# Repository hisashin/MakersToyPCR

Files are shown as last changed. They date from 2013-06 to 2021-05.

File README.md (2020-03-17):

## [We're fighting with COVID-19 by upgrading NinjaPCR into affordable Real-Time PCR.](https://github.com/hisashin/NinjaPCR/wiki/NinjaPCR's-fight-with-COVID-19)

NinjaPCR is Opensource(GPLv3) DNA Amplifier,Thermocycler Implementation for [Polymerase Chain Reaction](http://en.wikipedia.org/wiki/Polymerase_chain_reaction) developed by [Shingo Hisakawa](https://www.facebook.com/hisakawa) and [Mariko Hisakawa](https://www.facebook.com/maripo).<br />

Check [support site](https://ninjapcr.tori.st) for more infomations including how to [make](https://ninjapcr.tori.st/maker/) it. BOM is [here](https://docs.google.com/spreadsheets/d/1QYWESJrQ2N63OPvq1pnQvB-iVQkymN-hYeTYLx7xuOw/edit?usp=sharing).

(https://ninjapcr.tori.st)

Forked from [OpenPCR](https://github.com/jperfetto/OpenPCR).

Major changes from OpenPCR:<br />
01. Smaller and [easier to build](https://ninjapcr.tori.st/assy/index.html)<br />
02. Change platform from Adobe AIR to WiFi. Almost all PC and smartphones are supported<br />
03. LCD removed. Everything on Browser<br />
04. Keep precision from low to high temperature<br />
05. Auto update for new features (ex. IFTTT support scheduled)<br />
06. It's still [on sale](https://shop.tori.st) (OpenPCR is [discontinued](https://www.chaibio.com/openpcr))

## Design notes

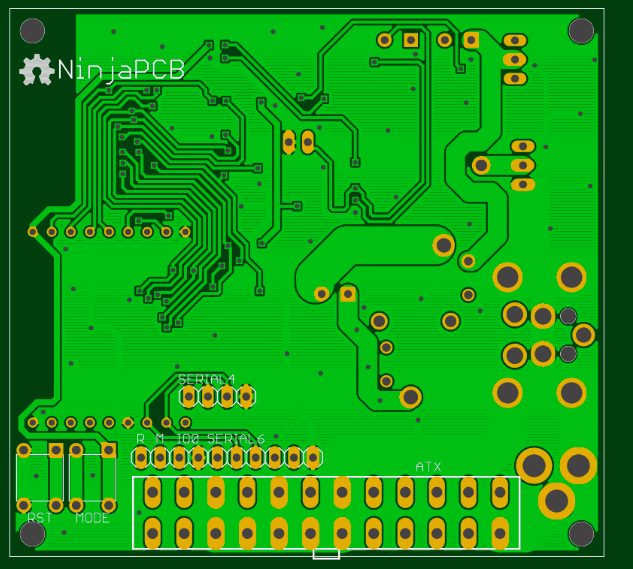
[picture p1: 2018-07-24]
eagle/NinjaPCB_ver2.2-bottom.png

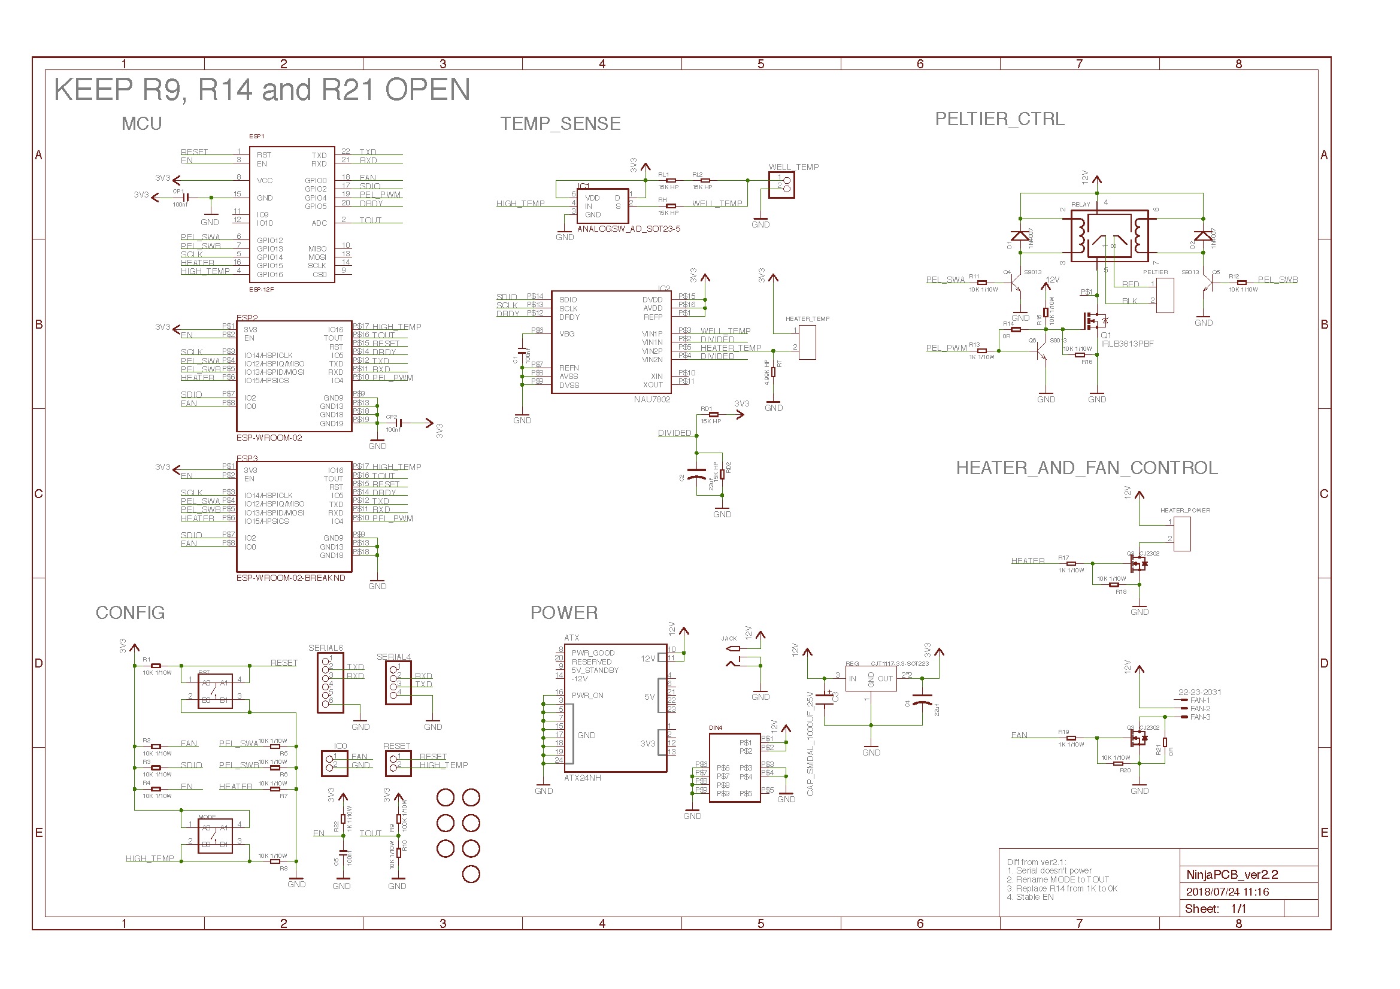
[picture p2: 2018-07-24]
eagle/NinjaPCB_ver2.2-sch.jpeg

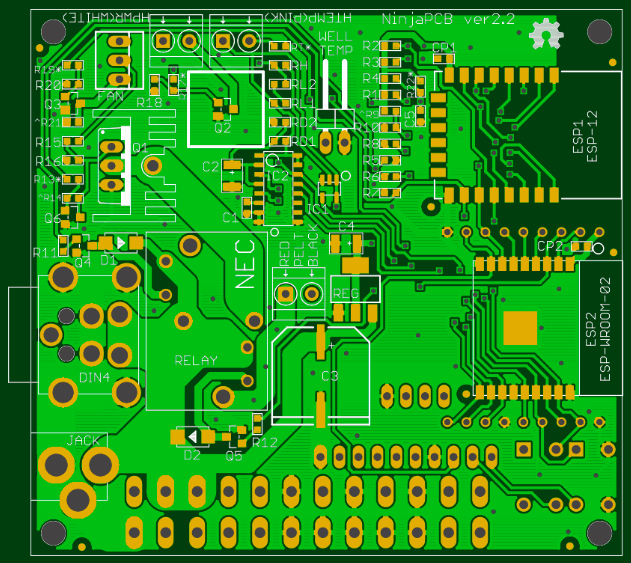
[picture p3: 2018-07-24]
eagle/NinjaPCB_ver2.2-top.png

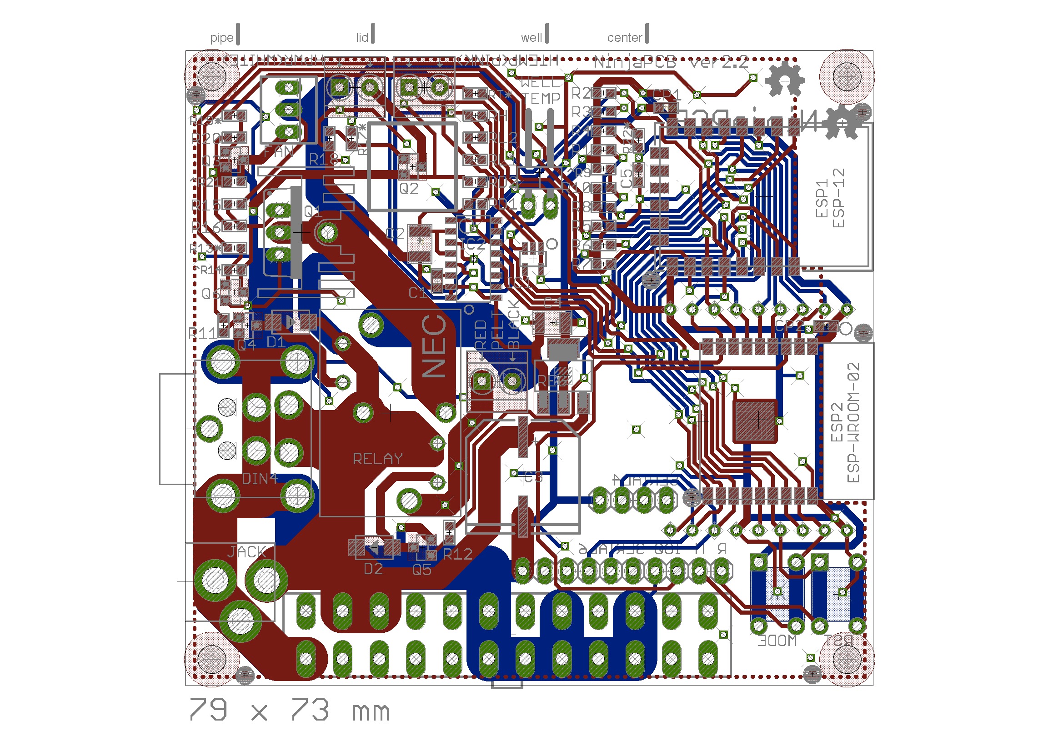
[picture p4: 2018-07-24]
eagle/NinjaPCB_ver2.2-brd.jpeg

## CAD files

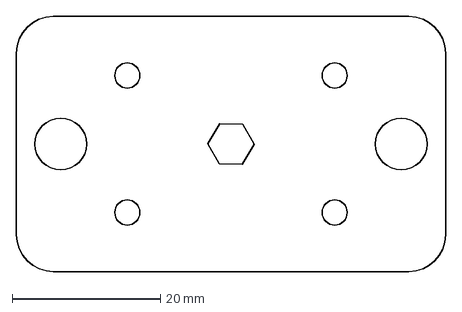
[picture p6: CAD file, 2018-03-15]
cad/2d/2x2-MooMoo/w4001_heater-lift.dxf
58.0 x 34.5 mm

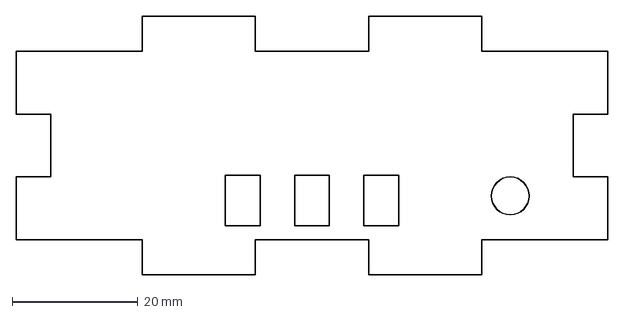
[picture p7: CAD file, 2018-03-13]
cad/2d/4x4-NinNin/w1003_cover-back.dxf
94.0 x 41.0 mm

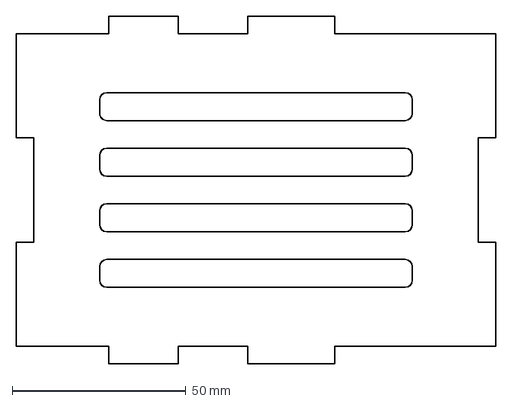
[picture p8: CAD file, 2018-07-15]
cad/2d/dxf-t5.0mm/LGA115x-kit/w2004.dxf
138.1 x 100.0 mm

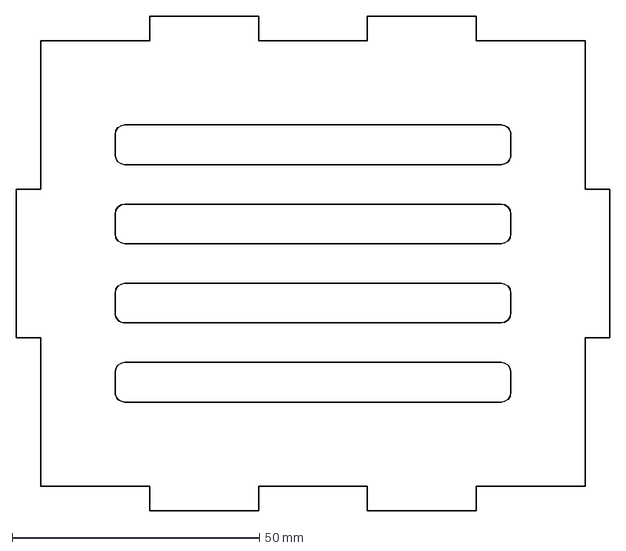
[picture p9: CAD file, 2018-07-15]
cad/2d/dxf-t5.0mm/w2005.dxf
120.0 x 100.0 mm

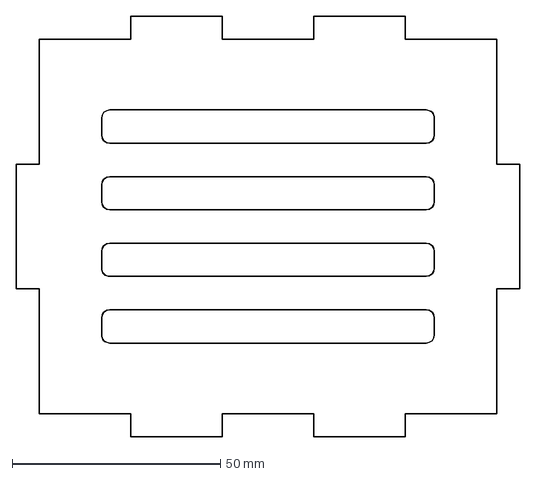
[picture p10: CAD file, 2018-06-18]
cad/2d/dxf-t5.5mm/LGA115x-kit/w2005.dxf
121.0 x 101.0 mm

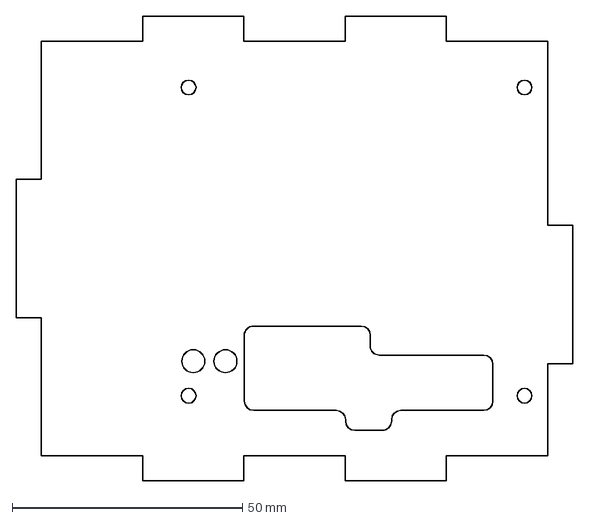
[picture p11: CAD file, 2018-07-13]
cad/2d/dxf-t5.5mm/LGA115x-maker/w2003-maker.dxf
121.0 x 101.0 mm

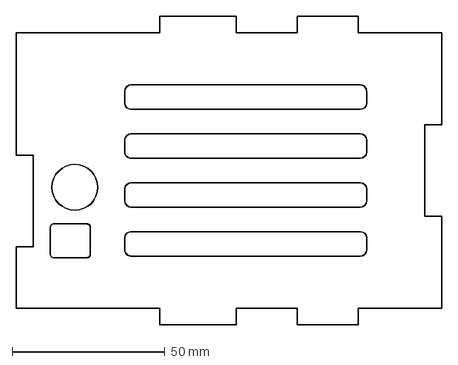
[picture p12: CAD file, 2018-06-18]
cad/2d/dxf-t5.5mm/LGA775-kit/w2006.dxf
139.1 x 101.0 mm

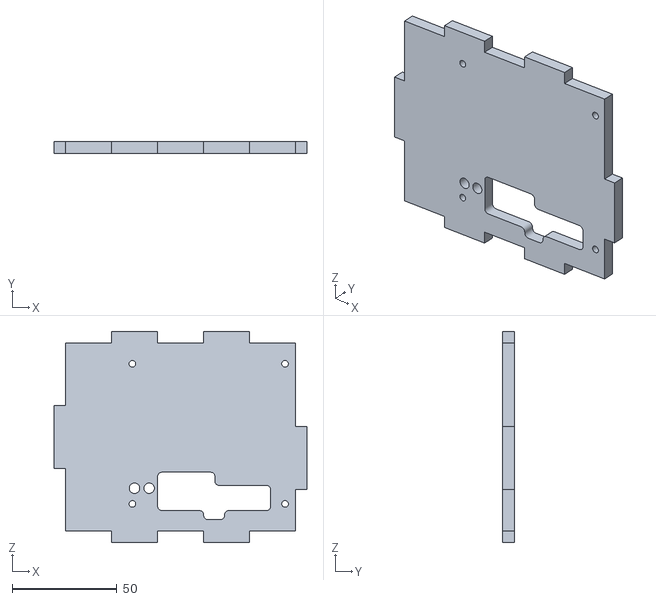
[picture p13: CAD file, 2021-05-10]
cad/3d/w2003a_body-front-ver2.1-maker.stl
121.0 x 5.50 x 101.0

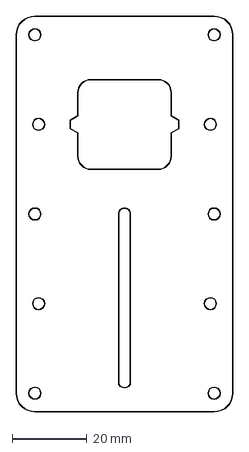
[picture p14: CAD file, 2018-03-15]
cad/2d/2x2-MooMoo/w4002-body-top.dxf
58.0 x 106.0 mm

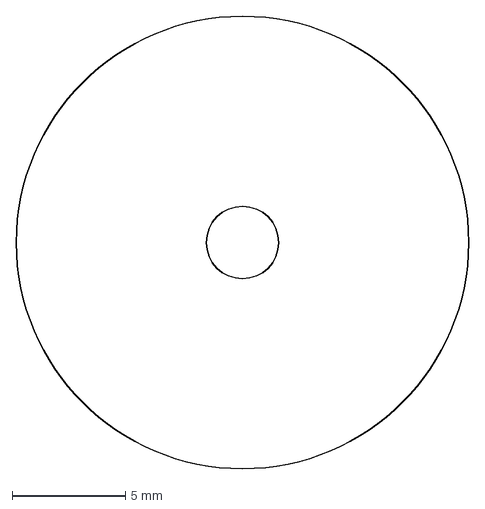
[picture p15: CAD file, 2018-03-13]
cad/2d/4x4-NinNin/w3003_latch-base.dxf
20.0 x 20.0 mm

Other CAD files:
cad/2d/2x2-MooMoo/w4004-heatsink-hold.dxf
cad/2d/4x4-NinNin/w1005_cover-sides.dxf
cad/2d/4x4-NinNin/w2001_heatsink-hang.dxf
cad/2d/4x4-NinNin/w2002_body-top.dxf
cad/2d/4x4-NinNin/w2004_body-left.dxf
cad/2d/4x4-NinNin/w2006_body-front.dxf
cad/2d/4x4-NinNin/w2008_body-hinges.dxf
cad/2d/dxf-t5.0mm/LGA115x-kit/w1001.dxf
cad/2d/dxf-t5.0mm/LGA115x-kit/w1002.dxf
cad/2d/dxf-t5.0mm/LGA115x-kit/w1003-kit.dxf
cad/2d/dxf-t5.0mm/LGA115x-kit/w1004-kit.dxf
cad/2d/dxf-t5.0mm/LGA115x-kit/w1005x2.dxf
cad/2d/dxf-t5.0mm/LGA115x-kit/w1006.dxf
cad/2d/dxf-t5.0mm/LGA115x-kit/w2001-LGA115x.dxf
cad/2d/dxf-t5.0mm/LGA115x-kit/w2002-LGA115x-kit.dxf
cad/2d/dxf-t5.0mm/LGA115x-kit/w2003-kit.dxf
cad/2d/dxf-t5.0mm/LGA115x-kit/w2003.dxf
cad/2d/dxf-t5.0mm/LGA115x-kit/w2006.dxf
cad/2d/dxf-t5.0mm/LGA115x-kit/w2007.dxf
cad/2d/dxf-t5.0mm/LGA115x-maker/w1001.dxf
cad/2d/dxf-t5.0mm/LGA115x-maker/w1002.dxf
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

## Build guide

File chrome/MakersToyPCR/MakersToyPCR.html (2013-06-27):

Makers Toy PCR

 Add a new experiment

 Re-run an experiment

Searching for a device...

Open Download Page



 Initial Step

 Final Step

Name your experiment

Experiment saved!

Delete Experiment?

Deleted!

Time remaining:

Status | Current Temperature
Cycle - / - | Lid: | °C
| Block: | °C
| Lid: Peltier:

Your Makers Toy PCR is unplugged from the computer.
Plug in your Makers Toy PCR to get updated information on your run.

Stop PCR?

Version
Makers Toy PCR App
http://www.tori.st
Email us: all@tori.st

Drag the slider to adjust the screen's contrast.

Ready. Steady. Go!

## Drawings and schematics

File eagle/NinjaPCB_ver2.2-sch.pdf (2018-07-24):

# TEMP_SENSE

MCU | PELTIER_CTRL

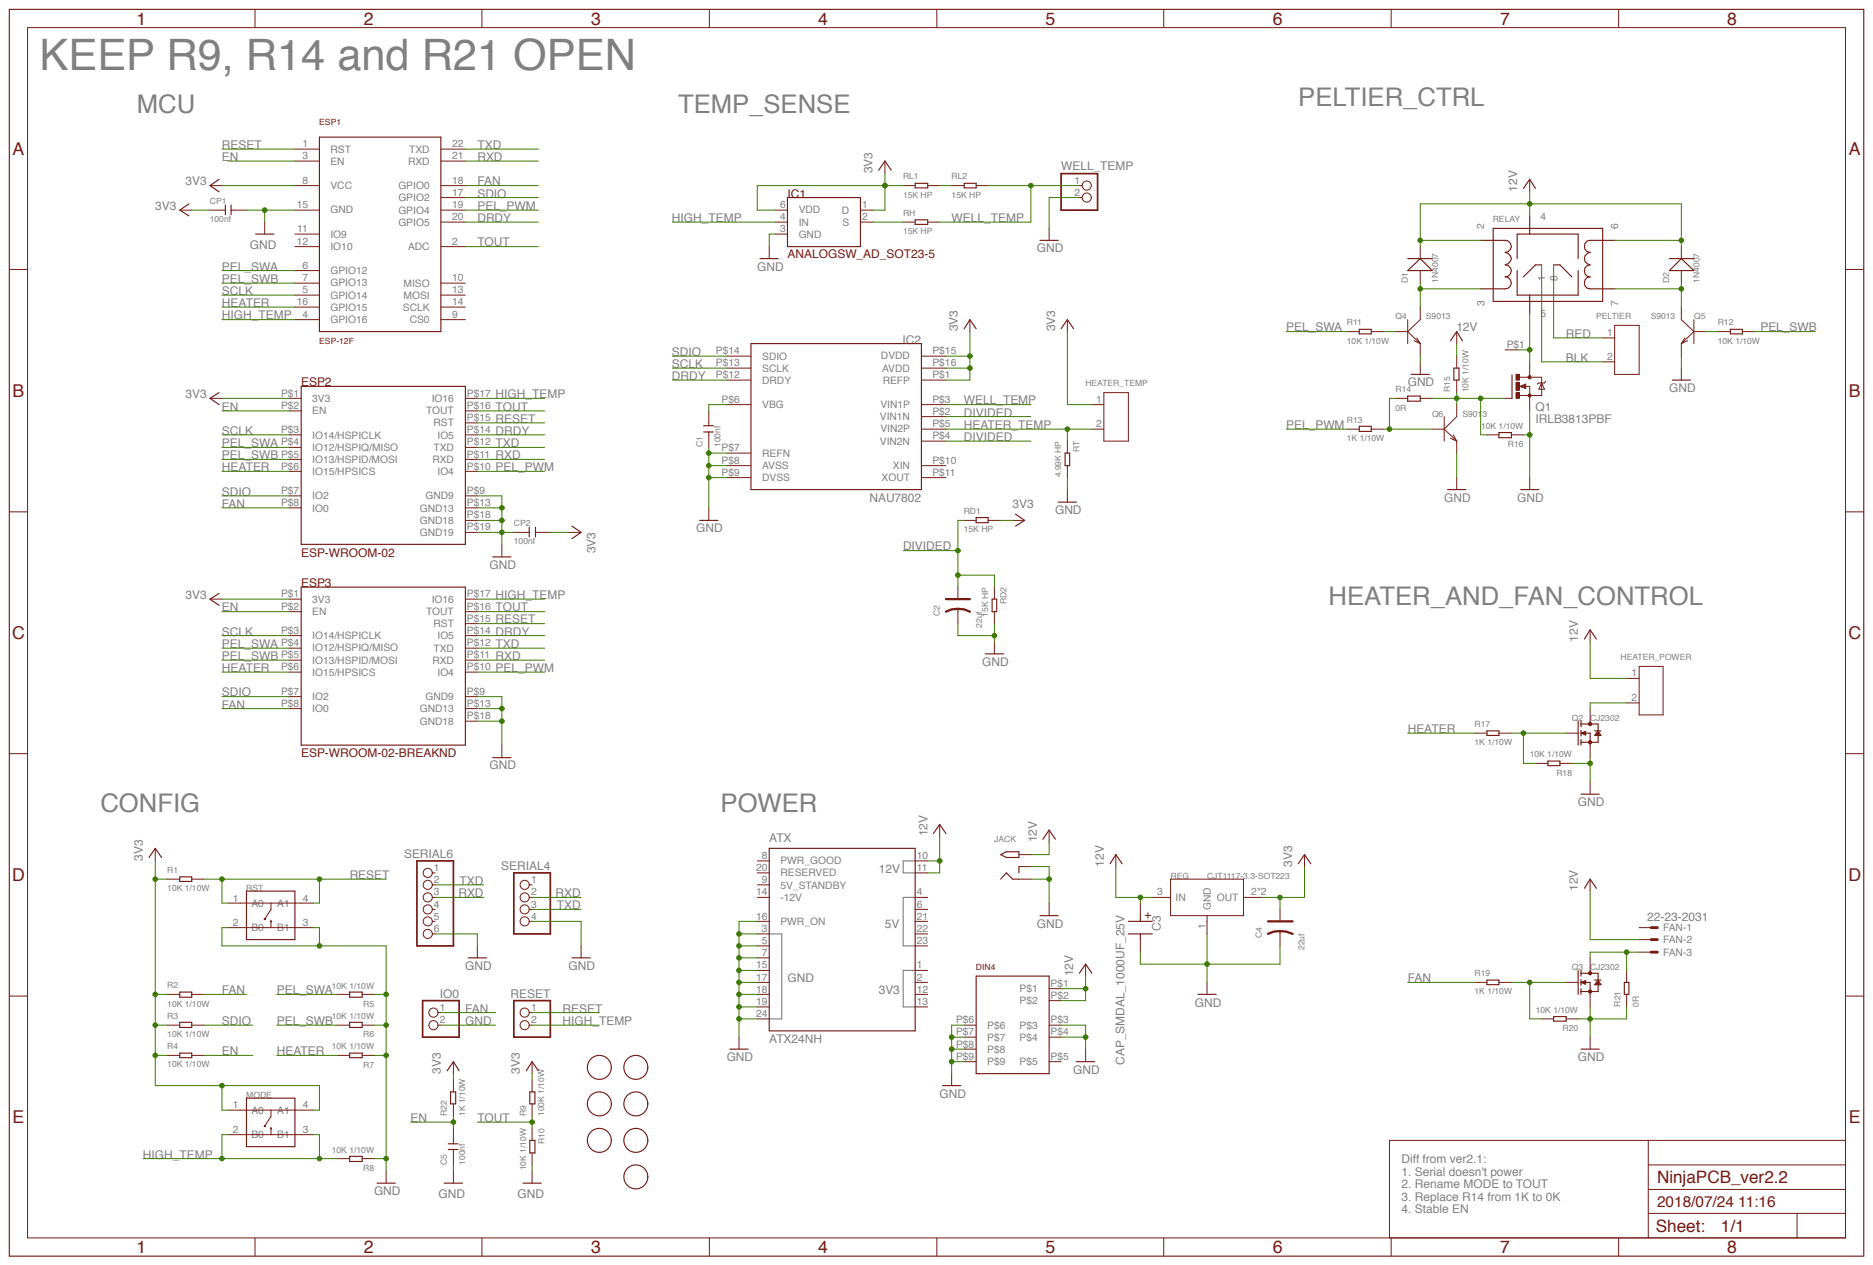
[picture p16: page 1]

Diff from ver2.1: 1. Serial doesn't power 2. Rename MODE to TOUT 3. Replace R14 from 1K to 0K 4. Stable EN

Sheet: 1/1

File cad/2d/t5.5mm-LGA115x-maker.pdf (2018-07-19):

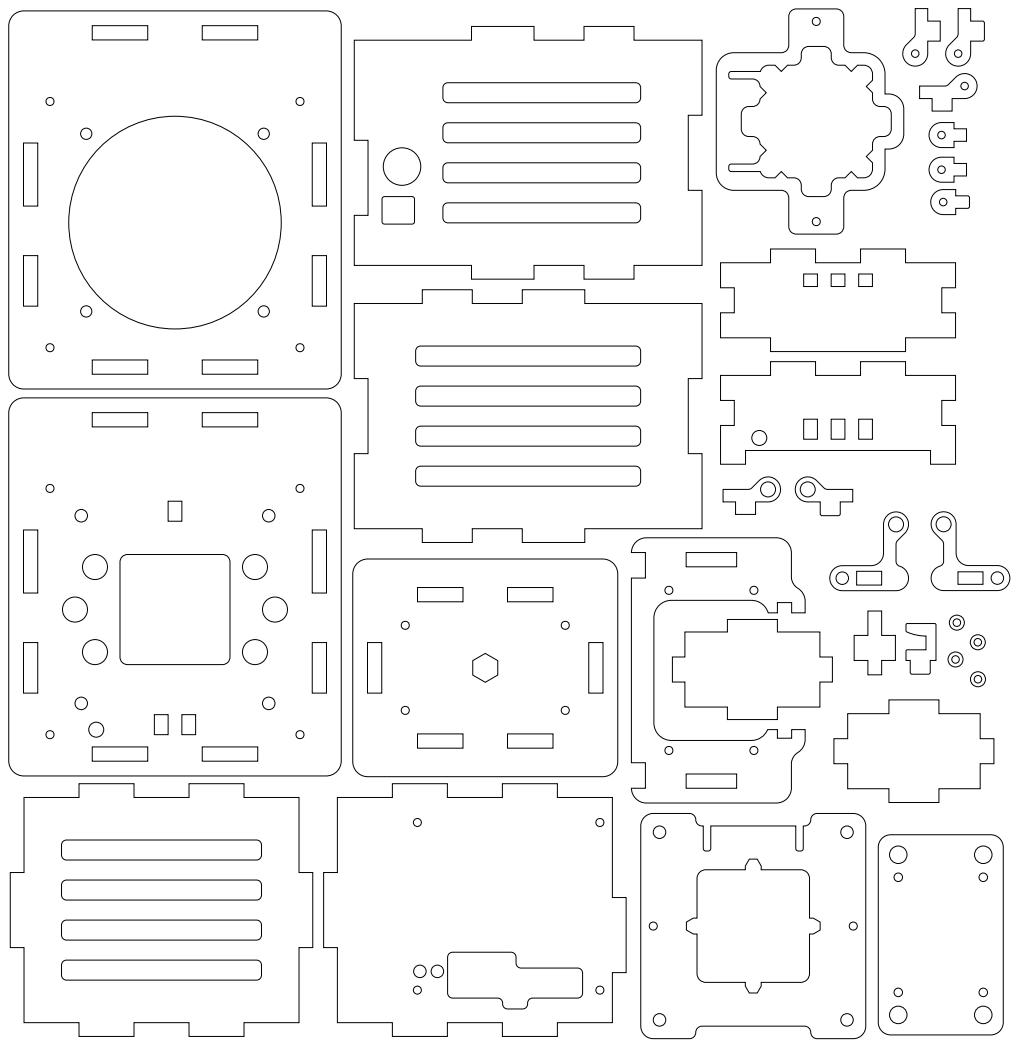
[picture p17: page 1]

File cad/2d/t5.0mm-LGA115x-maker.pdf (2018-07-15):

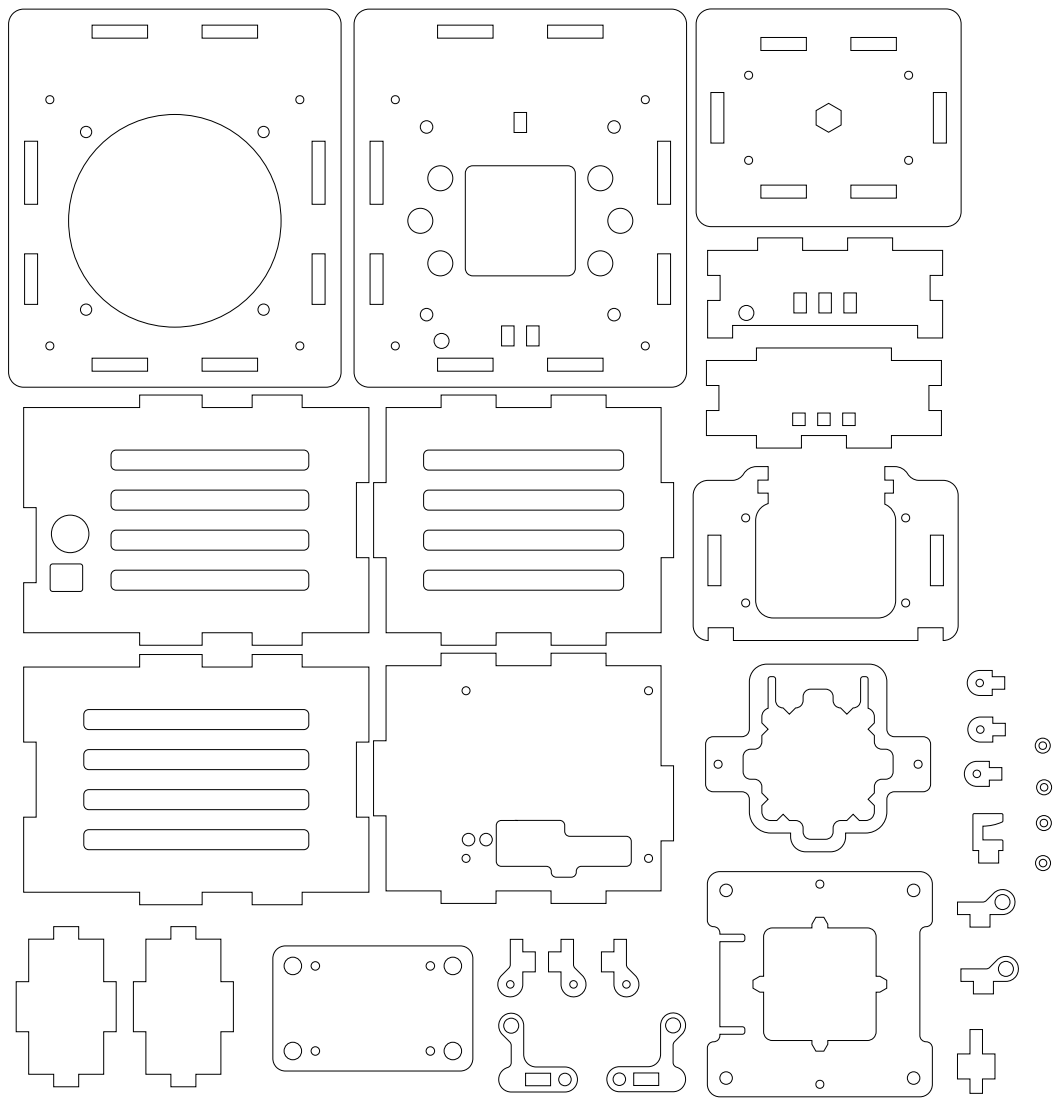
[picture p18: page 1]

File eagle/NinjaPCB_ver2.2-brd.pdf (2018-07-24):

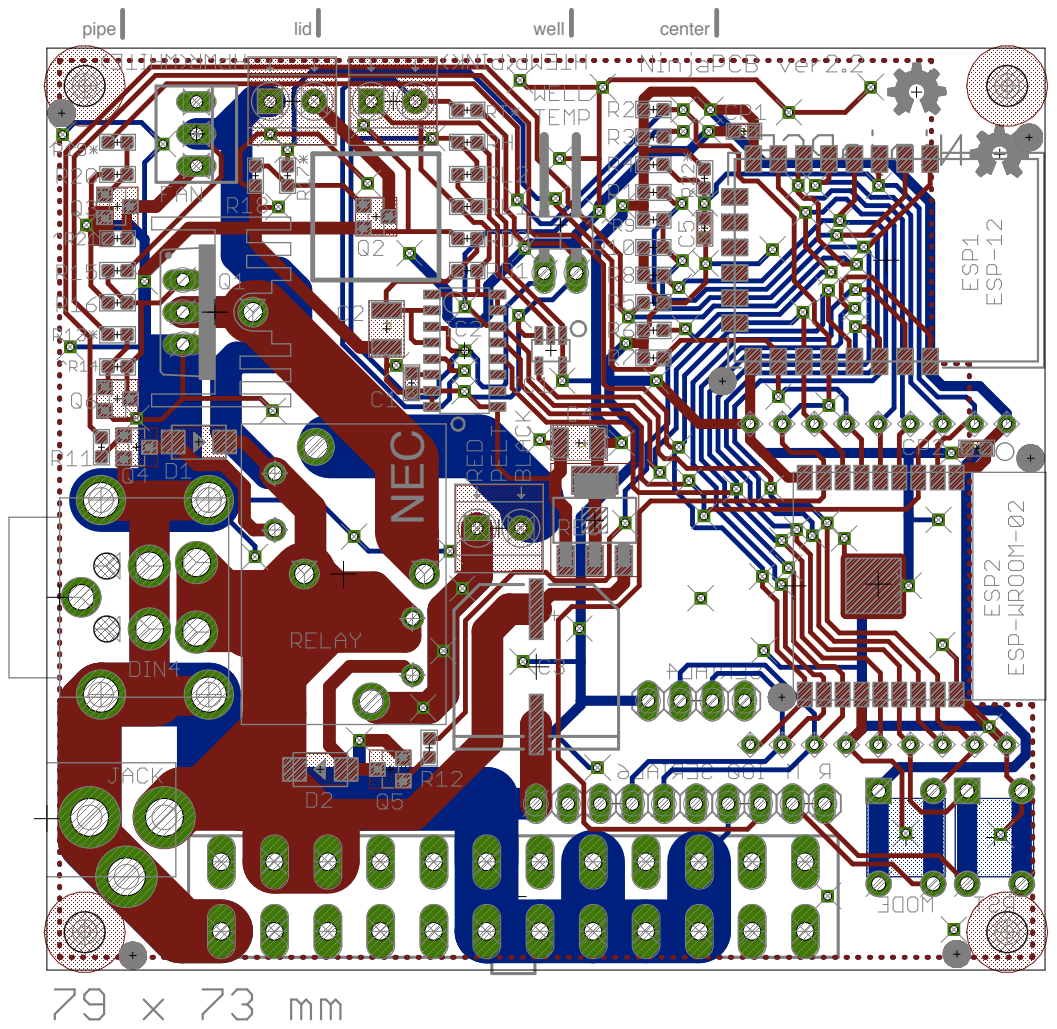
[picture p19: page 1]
NEC; pipe; lid; well; center

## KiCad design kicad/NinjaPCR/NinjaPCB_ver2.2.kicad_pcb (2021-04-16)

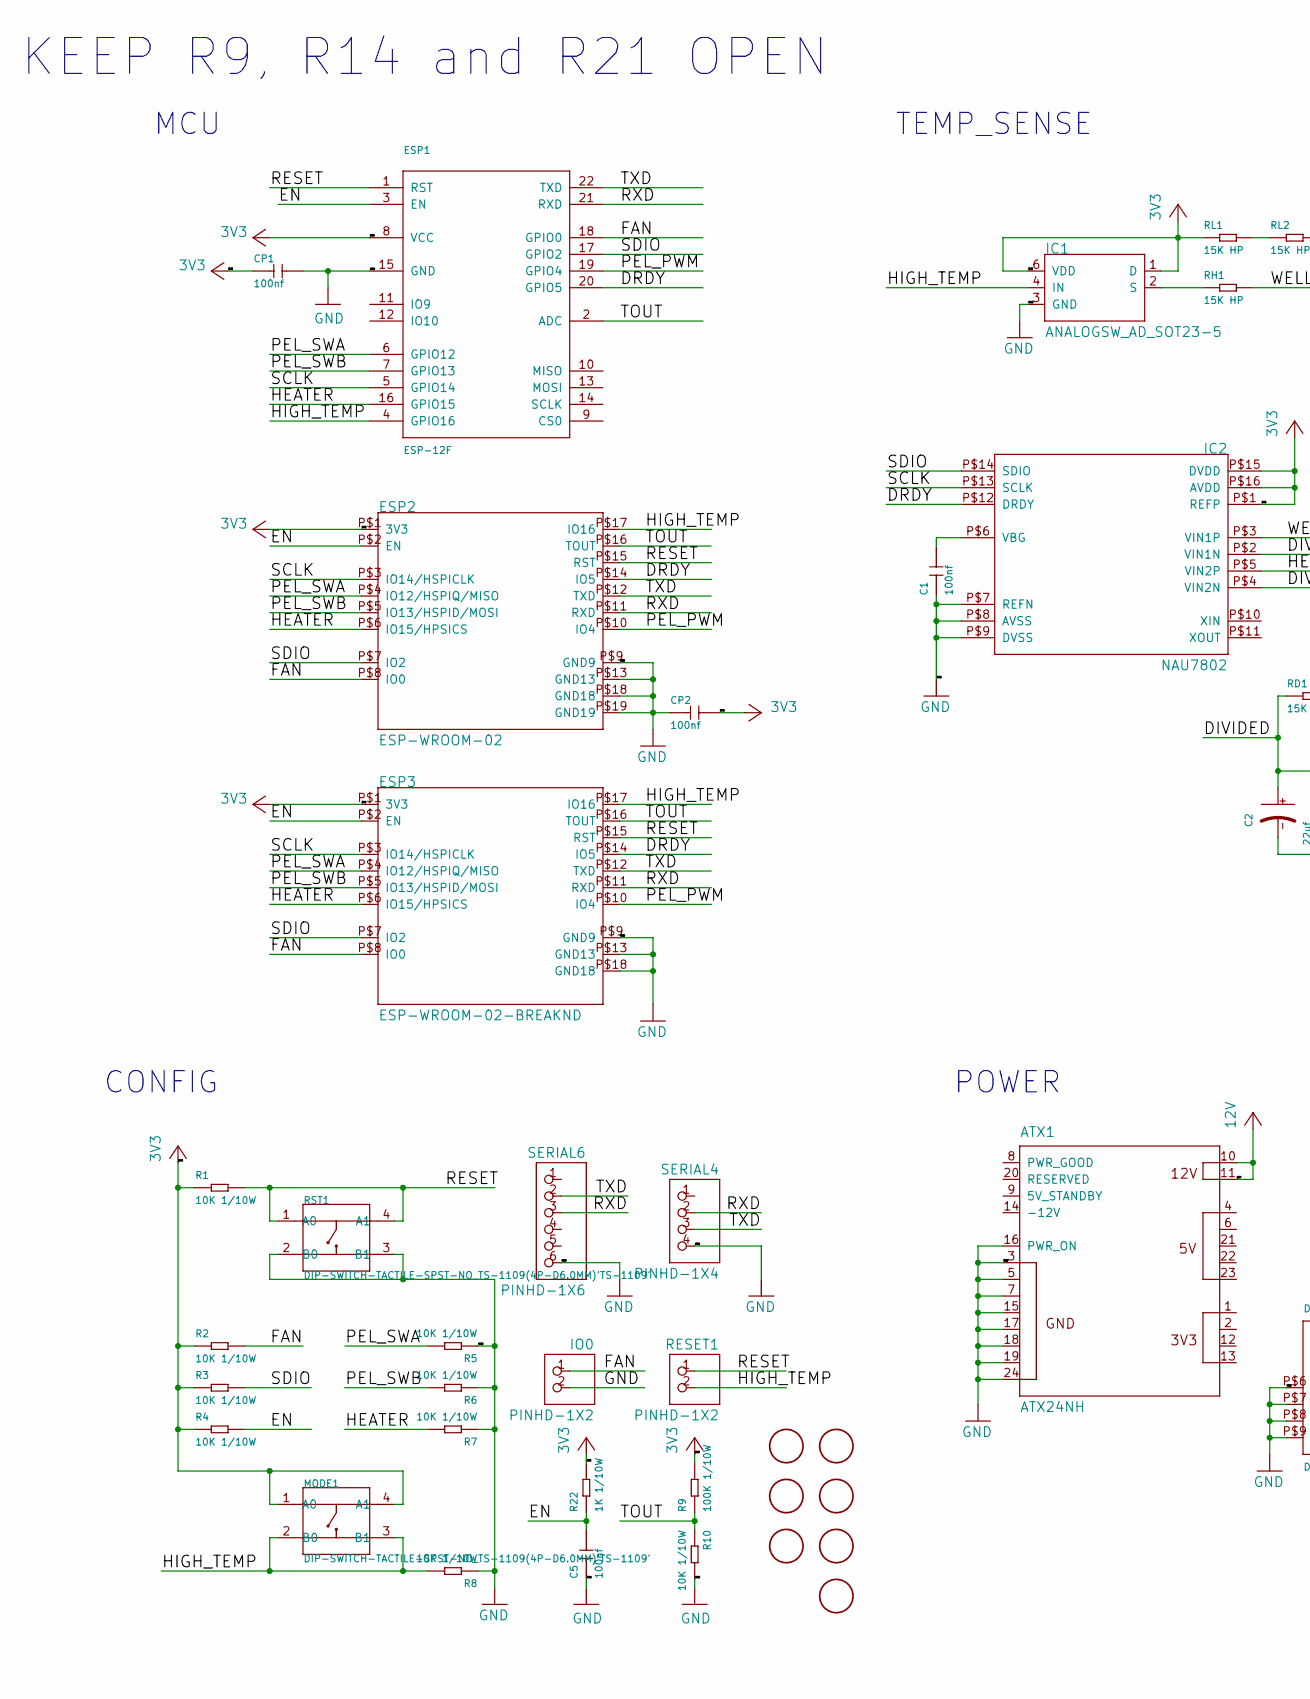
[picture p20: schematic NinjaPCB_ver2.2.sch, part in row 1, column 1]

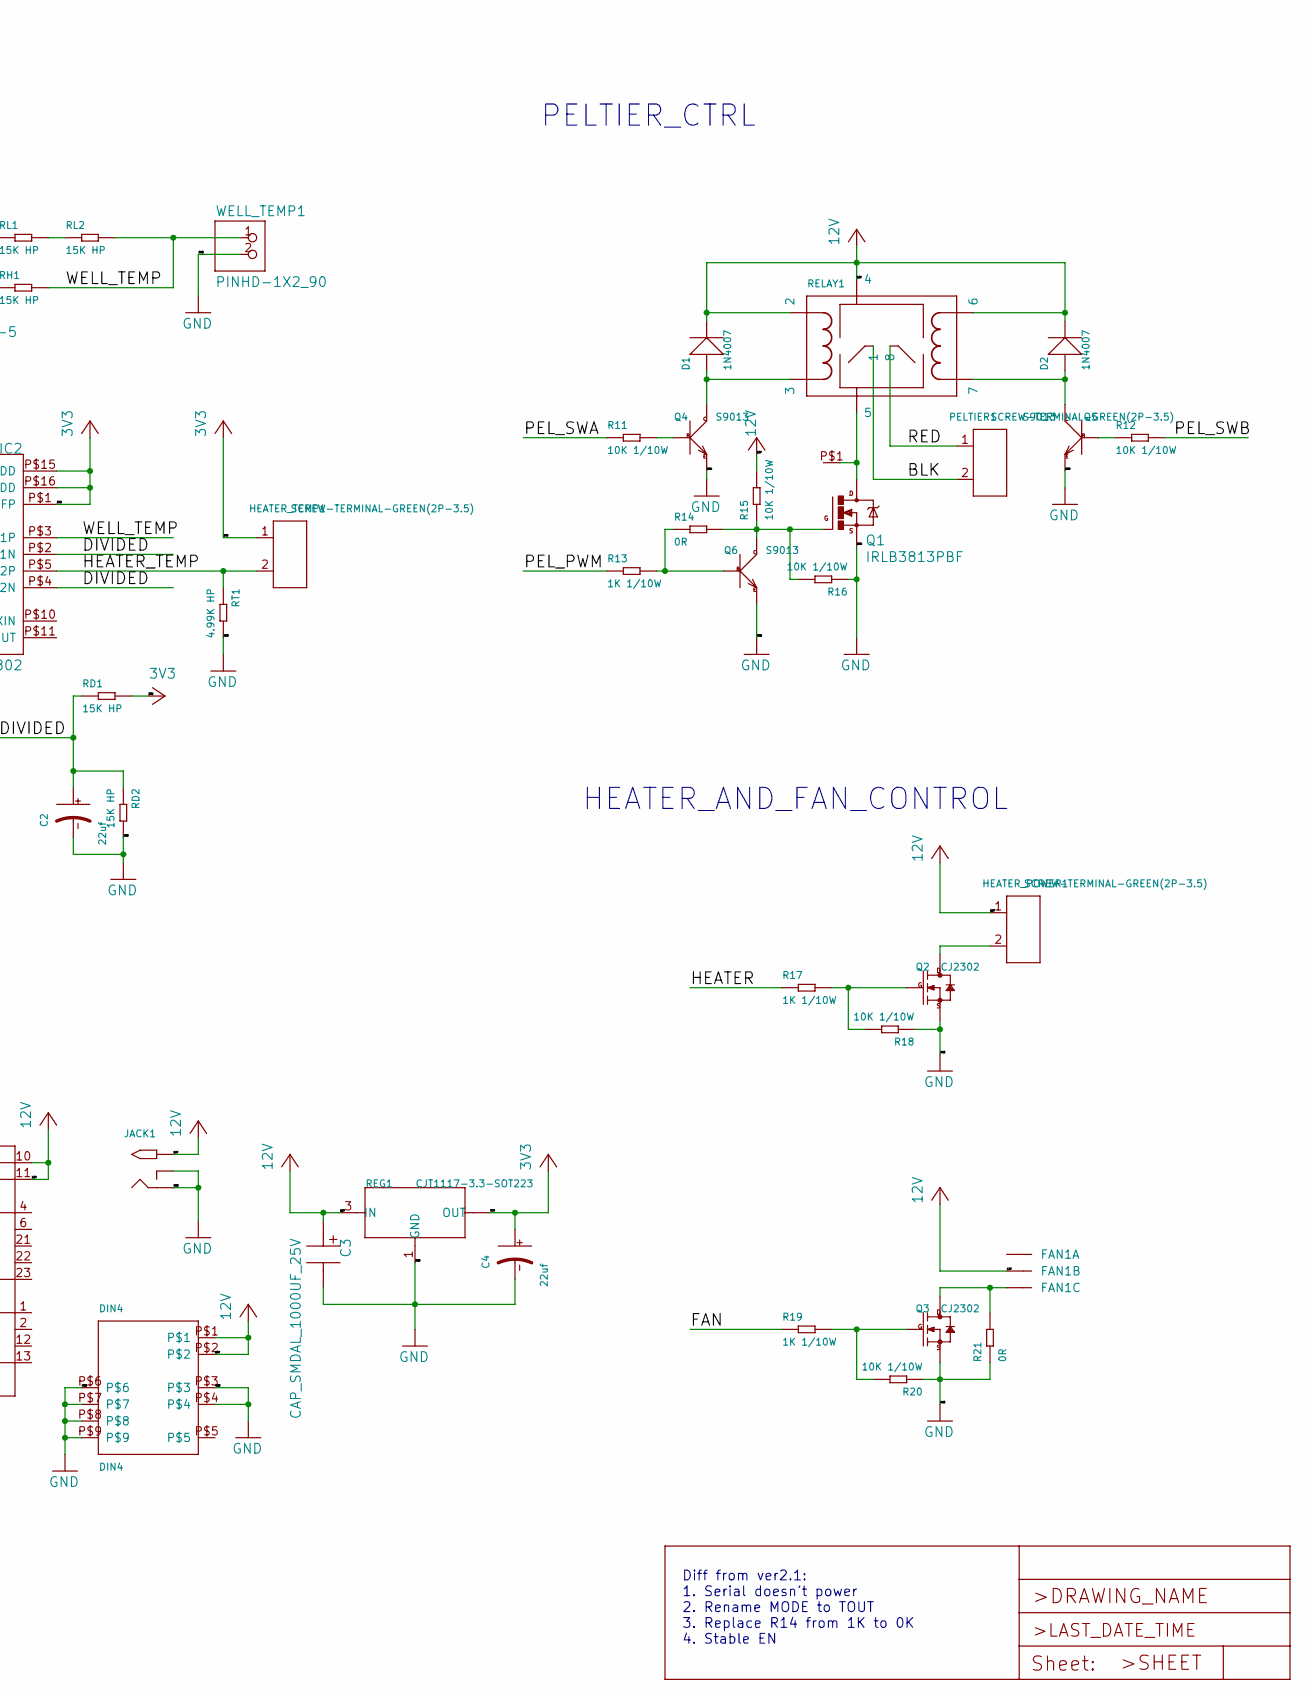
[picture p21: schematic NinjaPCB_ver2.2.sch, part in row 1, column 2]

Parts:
ATX1: ATX24NH; ATX24
C1, C5: 100nf; C0603
C2, C4: 22uf; AVX-B
C3: CAP_SMDAL_1000UF_25V; CAP_SMD_AL_D125
CP1, CP2: 100nf; C0603
D1, D2: 1N4007; DO-214AC
DIN4: DIN4
ESP1: ESP-12F
ESP2: ESP-WROOM-02
ESP3: ESP-WROOM-02-BREAKND; ESP-WROOM-02-BREAK-NODETAIL
FAN1: 22-23-2031
HEATER_POWER1: SCREW-TERMINAL-GREEN(2P-3.5); H2-3.5-7.0X7.0MM
HEATER_TEMP1: SCREW-TERMINAL-GREEN(2P-3.5); H2-3.5-7.0X7.0MM
HEATSINK1: HEAT111PB015; HEAT11PB015
IC1: ANALOGSW_AD_SOT23-5; SOT23-5
IC2: NAU7802; SOP-16
IO0: PINHD-1X2; 1X02
JACK1: 2.1MMJACKTHM-NOOUT; PJ-102A-NOOUT
MODE1: DIP-SWITCH-TACTILE-SPST-NO_TS-1109(4P-D6.0MM)'TS-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; SW4-6.0X6.0X5.0MM
PELTIER1: SCREW-TERMINAL-GREEN(2P-3.5); H2-3.5-7.0X7.0MM
Q1: IRLB3813PBF; TO220BV
Q2, Q3: CJ2302; SOT-23
Q4, Q5, Q6: S9013; SOT-23
R1, R2, R3, R4, R5, R6, R7, R8, R10, R11, R12, R15, R16, R18, R20: 10K 1/10W; R0603
R9: 100K 1/10W; R0603
R13, R17, R19, R22: 1K 1/10W; R0603
R14, R21: 0R; R0603
RD1, RD2: 15K HP; R0603
REG1: CJT1117-3.3-SOT223; SOT-223
RELAY1: NEC-RELAY2EP2; NEC-EP2
RESET1: PINHD-1X2; 1X02
RH1: 15K HP; R0603
RL1, RL2: 15K HP; R0603
RST1: DIP-SWITCH-TACTILE-SPST-NO_TS-1109(4P-D6.0MM)'TS-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; SW4-6.0X6.0X5.0MM
RT1: 4.99K HP; R0603
SERIAL4: PINHD-1X4; 1X04
SERIAL6: PINHD-1X6; 1X06
U$3, U$4, U$5, U$7, U$8, U$9, U$10: FIDUCIAL; FIDUCIAL_1MM
WELL_TEMP1: PINHD-1X2_90; 1X02_90

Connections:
/BLK: PELTIER1.2, RELAY1.P$1 (1)
/DIVIDED: C2.+, IC2.P$2 (VIN1N), IC2.P$4 (VIN2N), RD1.1, RD2.1
/DRDY: ESP1.20 (GPIO5), ESP2.P$14 (IO5), ESP3.P$14 (IO5), IC2.P$12 (DRDY)
/EN: C5.2, ESP1.3 (EN), ESP2.P$2 (EN), ESP3.P$2 (EN), R4.2, R22.1
/FAN: ESP1.18 (GPIO0), ESP2.P$8 (IO0), ESP3.P$8 (IO0), IO0.1, R2.2, R19.1
/HEATER: ESP1.16 (GPIO15), ESP2.P$6 (IO15/HPSICS), ESP3.P$6 (IO15/HPSICS), R7.2, R17.1
/HEATER_TEMP: HEATER_TEMP1.2, IC2.P$5 (VIN2P), RT1.1
/HIGH_TEMP: ESP1.4 (GPIO16), ESP2.P$17 (IO16), ESP3.P$17 (IO16), IC1.4 (IN), MODE1.2 (B0), MODE1.3 (B1), R8.2, RESET1.2
/PEL_PWM: ESP1.19 (GPIO4), ESP2.P$10 (IO4), ESP3.P$10 (IO4), R13.1
/PEL_SWA: ESP1.6 (GPIO12), ESP2.P$4 (IO12/HSPIQ/MISO), ESP3.P$4 (IO12/HSPIQ/MISO), R5.2, R11.1
/PEL_SWB: ESP1.7 (GPIO13), ESP2.P$5 (IO13/HSPID/MOSI), ESP3.P$5 (IO13/HSPID/MOSI), R6.2, R12.2
/RED: PELTIER1.1, RELAY1.P$8 (8)
/RESET: ESP1.1 (RST), ESP2.P$15 (RST), ESP3.P$15 (RST), R1.2, RESET1.1, RST1.1 (A0), RST1.4 (A1)
/RXD: ESP1.21 (RXD), ESP2.P$11 (RXD), ESP3.P$11 (RXD), SERIAL4.2, SERIAL6.3
/SCLK: ESP1.5 (GPIO14), ESP2.P$3 (IO14/HSPICLK), ESP3.P$3 (IO14/HSPICLK), IC2.P$13 (SCLK)
/SDIO: ESP1.17 (GPIO2), ESP2.P$7 (IO2), ESP3.P$7 (IO2), IC2.P$14 (SDIO), R3.2
/TOUT: ESP1.2 (ADC), ESP2.P$16 (TOUT), ESP3.P$16 (TOUT), R9.1, R10.1
/TXD: ESP1.22 (TXD), ESP2.P$12 (TXD), ESP3.P$12 (TXD), SERIAL4.3, SERIAL6.2
/WELL_TEMP: IC2.P$3 (VIN1P), RH1.2, RL2.2, WELL_TEMP1.1
GND: ATX1.3 (GND3), ATX1.5 (GND5), ATX1.7 (GND7), ATX1.15 (GND15), ATX1.16 (PWR_ON), ATX1.17 (GND17), ATX1.18 (GND18), ATX1.19 (GND19), ATX1.24 (GND24), C1.1, C2.-, C3.P$M, C4.-, C5.1, CP1.2, CP2.1, DIN4.P$3, DIN4.P$4, DIN4.P$6, DIN4.P$7, DIN4.P$8, DIN4.P$9, ESP1.15 (GND), ESP2.P$9 (GND9), ESP2.P$13 (GND13), ESP2.P$18 (GND18), ESP2.P$19 (GND19), ESP3.P$9 (GND9), ESP3.P$13 (GND13), ESP3.P$18 (GND18), IC1.3 (GND), IC2.P$7 (REFN), IC2.P$8 (AVSS), IC2.P$9 (DVSS), IO0.2, JACK1.RING, JACK1.RING_SW, Q1.S, Q2.2 (S), Q3.2 (S), Q4.2 (E), Q5.2 (E), Q6.2 (E), R5.1, R6.1, R7.1, R8.1, R10.2, R16.1, R18.1, R20.1, R21.1, RD2.2, REG1.1 (GND), RST1.2 (B0), RST1.3 (B1), RT1.2, SERIAL4.4, SERIAL6.6, WELL_TEMP1.2
unnamed: C1.2, IC2.P$6 (VBG)
unnamed: D1.1 (+), Q4.3 (C), RELAY1.P$3 (3)
unnamed: D2.1 (+), Q5.3 (C), RELAY1.P$7 (7)
unnamed: FAN1.3, Q3.3 (D), R21.2
unnamed: HEATER_POWER1.2, Q2.3 (D)
unnamed: HEATSINK1.P$1, Q1.D, RELAY1.P$5 (5)
unnamed: IC1.2 (S), RH1.1
unnamed: Q1.G, Q6.3 (C), R14.2, R15.1, R16.2
unnamed: Q2.1 (G), R17.2, R18.2
unnamed: Q3.1 (G), R19.2, R20.2
unnamed: Q4.1 (B), R11.2
unnamed: Q5.1 (B), R12.1
unnamed: Q6.1 (B), R13.2, R14.1
unnamed: RL1.2, RL2.1

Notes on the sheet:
TEMP_SENSE
HEATER_AND_FAN_CONTROL
PELTIER_CTRL
MCU
POWER
Diff from ver2.1: 1. Serial doesn't power 2. Rename MODE to TOUT 3. Replace R14 from 1K to 0K 4. Stable EN
CONFIG
KEEP R9, R14 and R21 OPEN

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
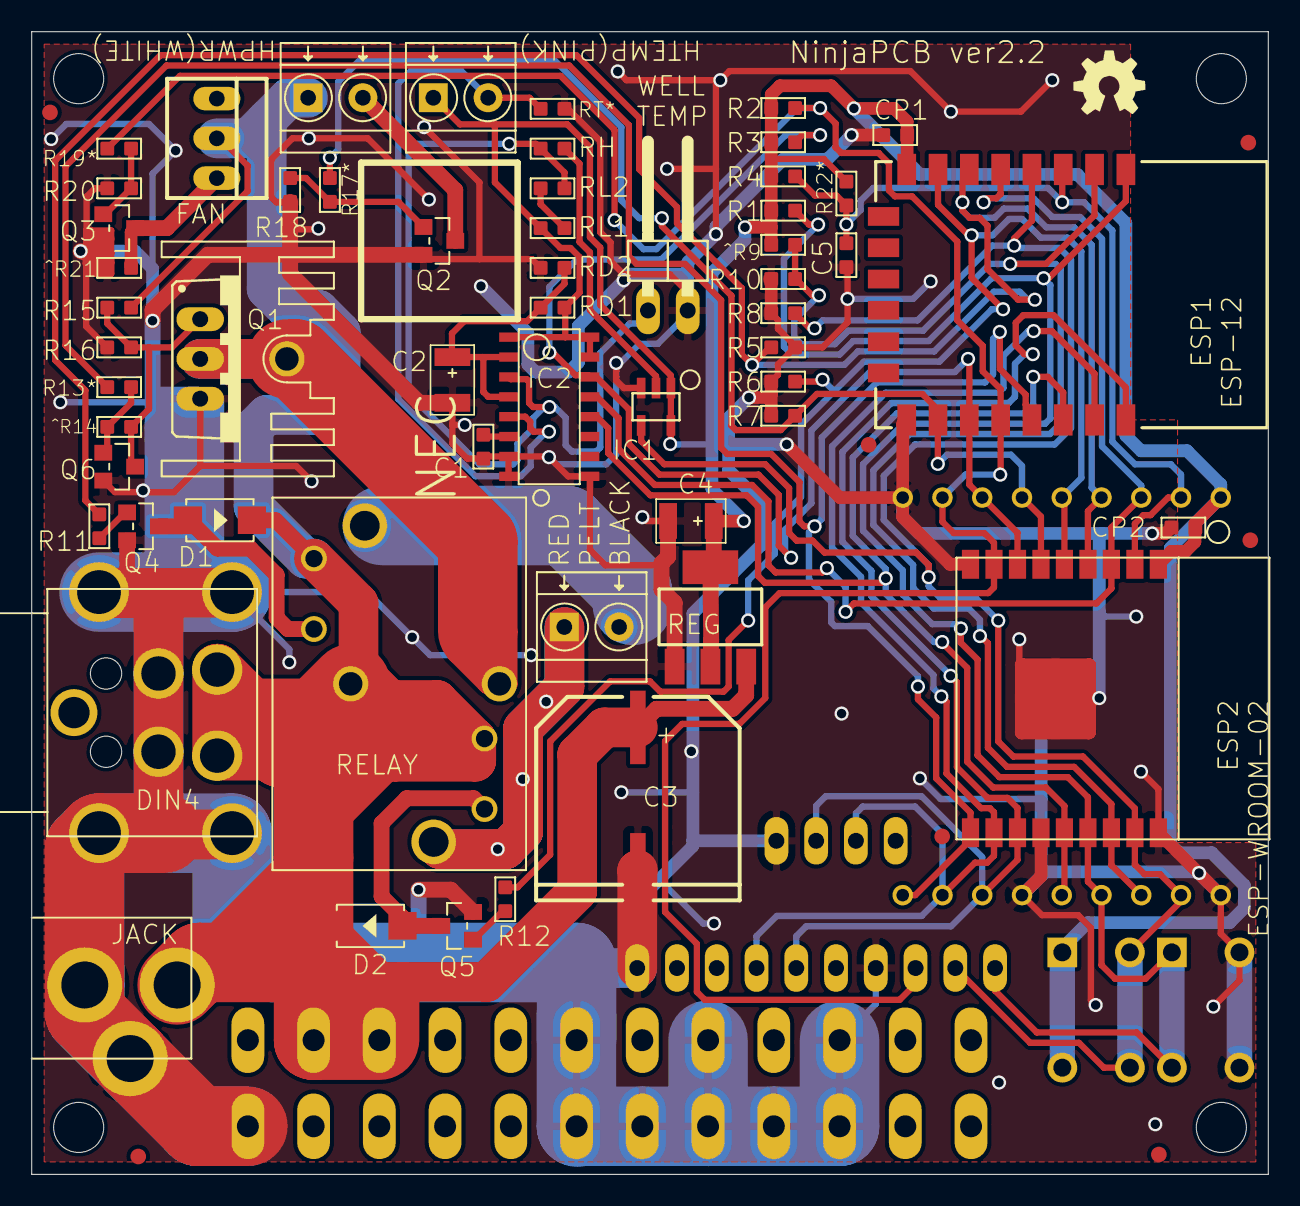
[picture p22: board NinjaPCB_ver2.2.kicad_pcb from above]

Board: 2 copper layers, 79.0 x 73.0 mm, 78 parts (0 on the bottom side), 35 nets.

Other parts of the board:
@HOLE0, @HOLE1, @HOLE2, @HOLE3: (no value)
U$1, U$2: OSHW_5MM

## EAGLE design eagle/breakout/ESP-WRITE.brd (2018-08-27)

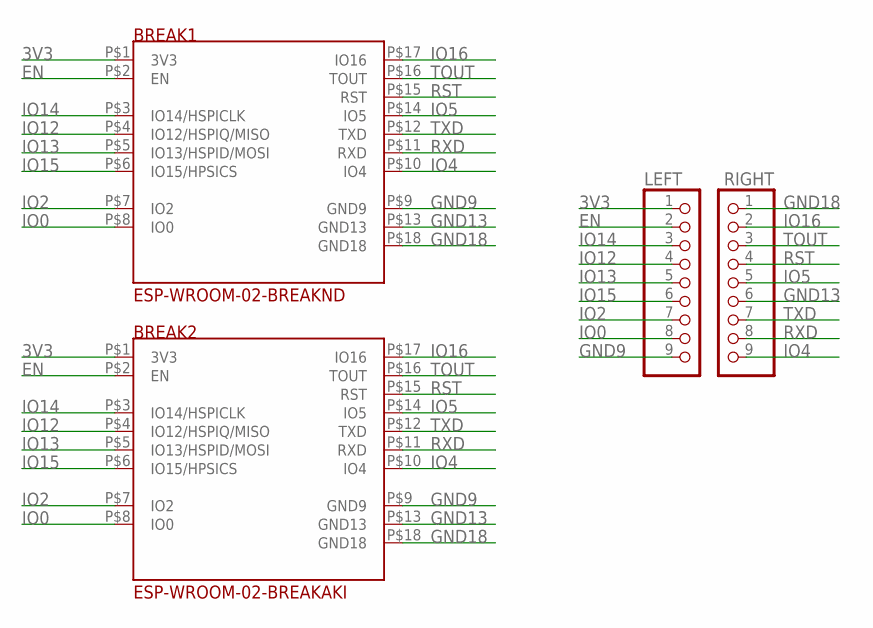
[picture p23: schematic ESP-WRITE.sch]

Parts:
BREAK1: ESP-WROOM-02-BREAKND; ESP-WROOM-02-BREAK-NODETAIL
BREAK2: ESP-WROOM-02-BREAKAKI; ESP-WROOM-02-AKI
LEFT: PINHD-1X9; 1X09
RIGHT: PINHD-1X9; 1X09

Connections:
3V3: BREAK1.P$1 (3V3), BREAK2.P$1 (3V3), LEFT.1
EN: BREAK1.P$2 (EN), BREAK2.P$2 (EN), LEFT.2
GND9: BREAK1.P$9 (GND9), BREAK2.P$9 (GND9), LEFT.9
GND13: BREAK1.P$13 (GND13), BREAK2.P$13 (GND13), RIGHT.6
GND18: BREAK1.P$18 (GND18), BREAK2.P$18 (GND18), RIGHT.1
IO0: BREAK1.P$8 (IO0), BREAK2.P$8 (IO0), LEFT.8
IO2: BREAK1.P$7 (IO2), BREAK2.P$7 (IO2), LEFT.7
IO4: BREAK1.P$10 (IO4), BREAK2.P$10 (IO4), RIGHT.9
IO5: BREAK1.P$14 (IO5), BREAK2.P$14 (IO5), RIGHT.5
IO12: BREAK1.P$4 (IO12/HSPIQ/MISO), BREAK2.P$4 (IO12/HSPIQ/MISO), LEFT.4
IO13: BREAK1.P$5 (IO13/HSPID/MOSI), BREAK2.P$5 (IO13/HSPID/MOSI), LEFT.5
IO14: BREAK1.P$3 (IO14/HSPICLK), BREAK2.P$3 (IO14/HSPICLK), LEFT.3
IO15: BREAK1.P$6 (IO15/HPSICS), BREAK2.P$6 (IO15/HPSICS), LEFT.6
IO16: BREAK1.P$17 (IO16), BREAK2.P$17 (IO16), RIGHT.2
RST: BREAK1.P$15 (RST), BREAK2.P$15 (RST), RIGHT.4
RXD: BREAK1.P$11 (RXD), BREAK2.P$11 (RXD), RIGHT.8
TOUT: BREAK1.P$16 (TOUT), BREAK2.P$16 (TOUT), RIGHT.3
TXD: BREAK1.P$12 (TXD), BREAK2.P$12 (TXD), RIGHT.7

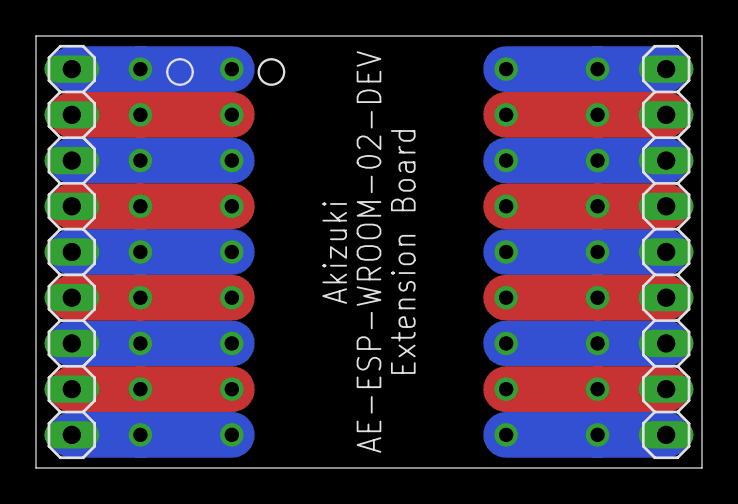
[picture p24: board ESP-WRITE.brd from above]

Board: 2 copper layers, 37.0 x 24.0 mm, 4 parts (0 on the bottom side), 18 nets.

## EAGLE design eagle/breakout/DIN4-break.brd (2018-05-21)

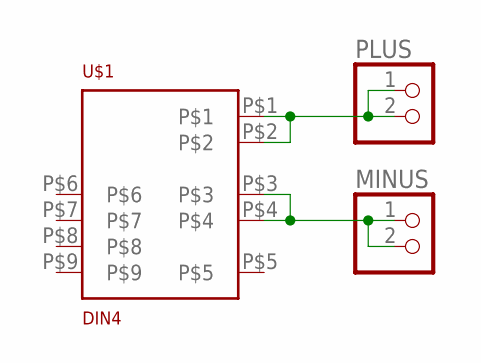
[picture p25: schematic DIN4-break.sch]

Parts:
MINUS: PINHD-1X2; 1X02
PLUS: PINHD-1X2; 1X02
U$1: DIN4

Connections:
MINUS: MINUS.1, MINUS.2, U$1.P$3, U$1.P$4
PLUS: PLUS.1, PLUS.2, U$1.P$1, U$1.P$2

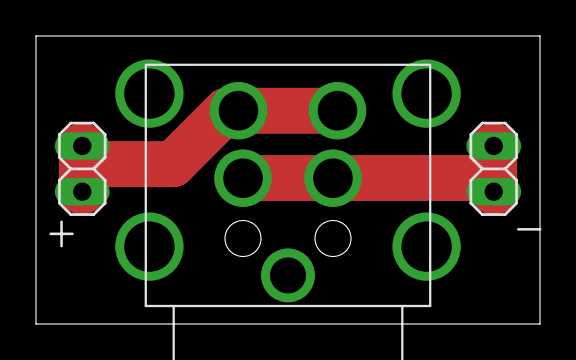
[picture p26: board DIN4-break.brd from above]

Board: 2 copper layers, 28.0 x 16.0 mm, 3 parts (0 on the bottom side), 2 nets.

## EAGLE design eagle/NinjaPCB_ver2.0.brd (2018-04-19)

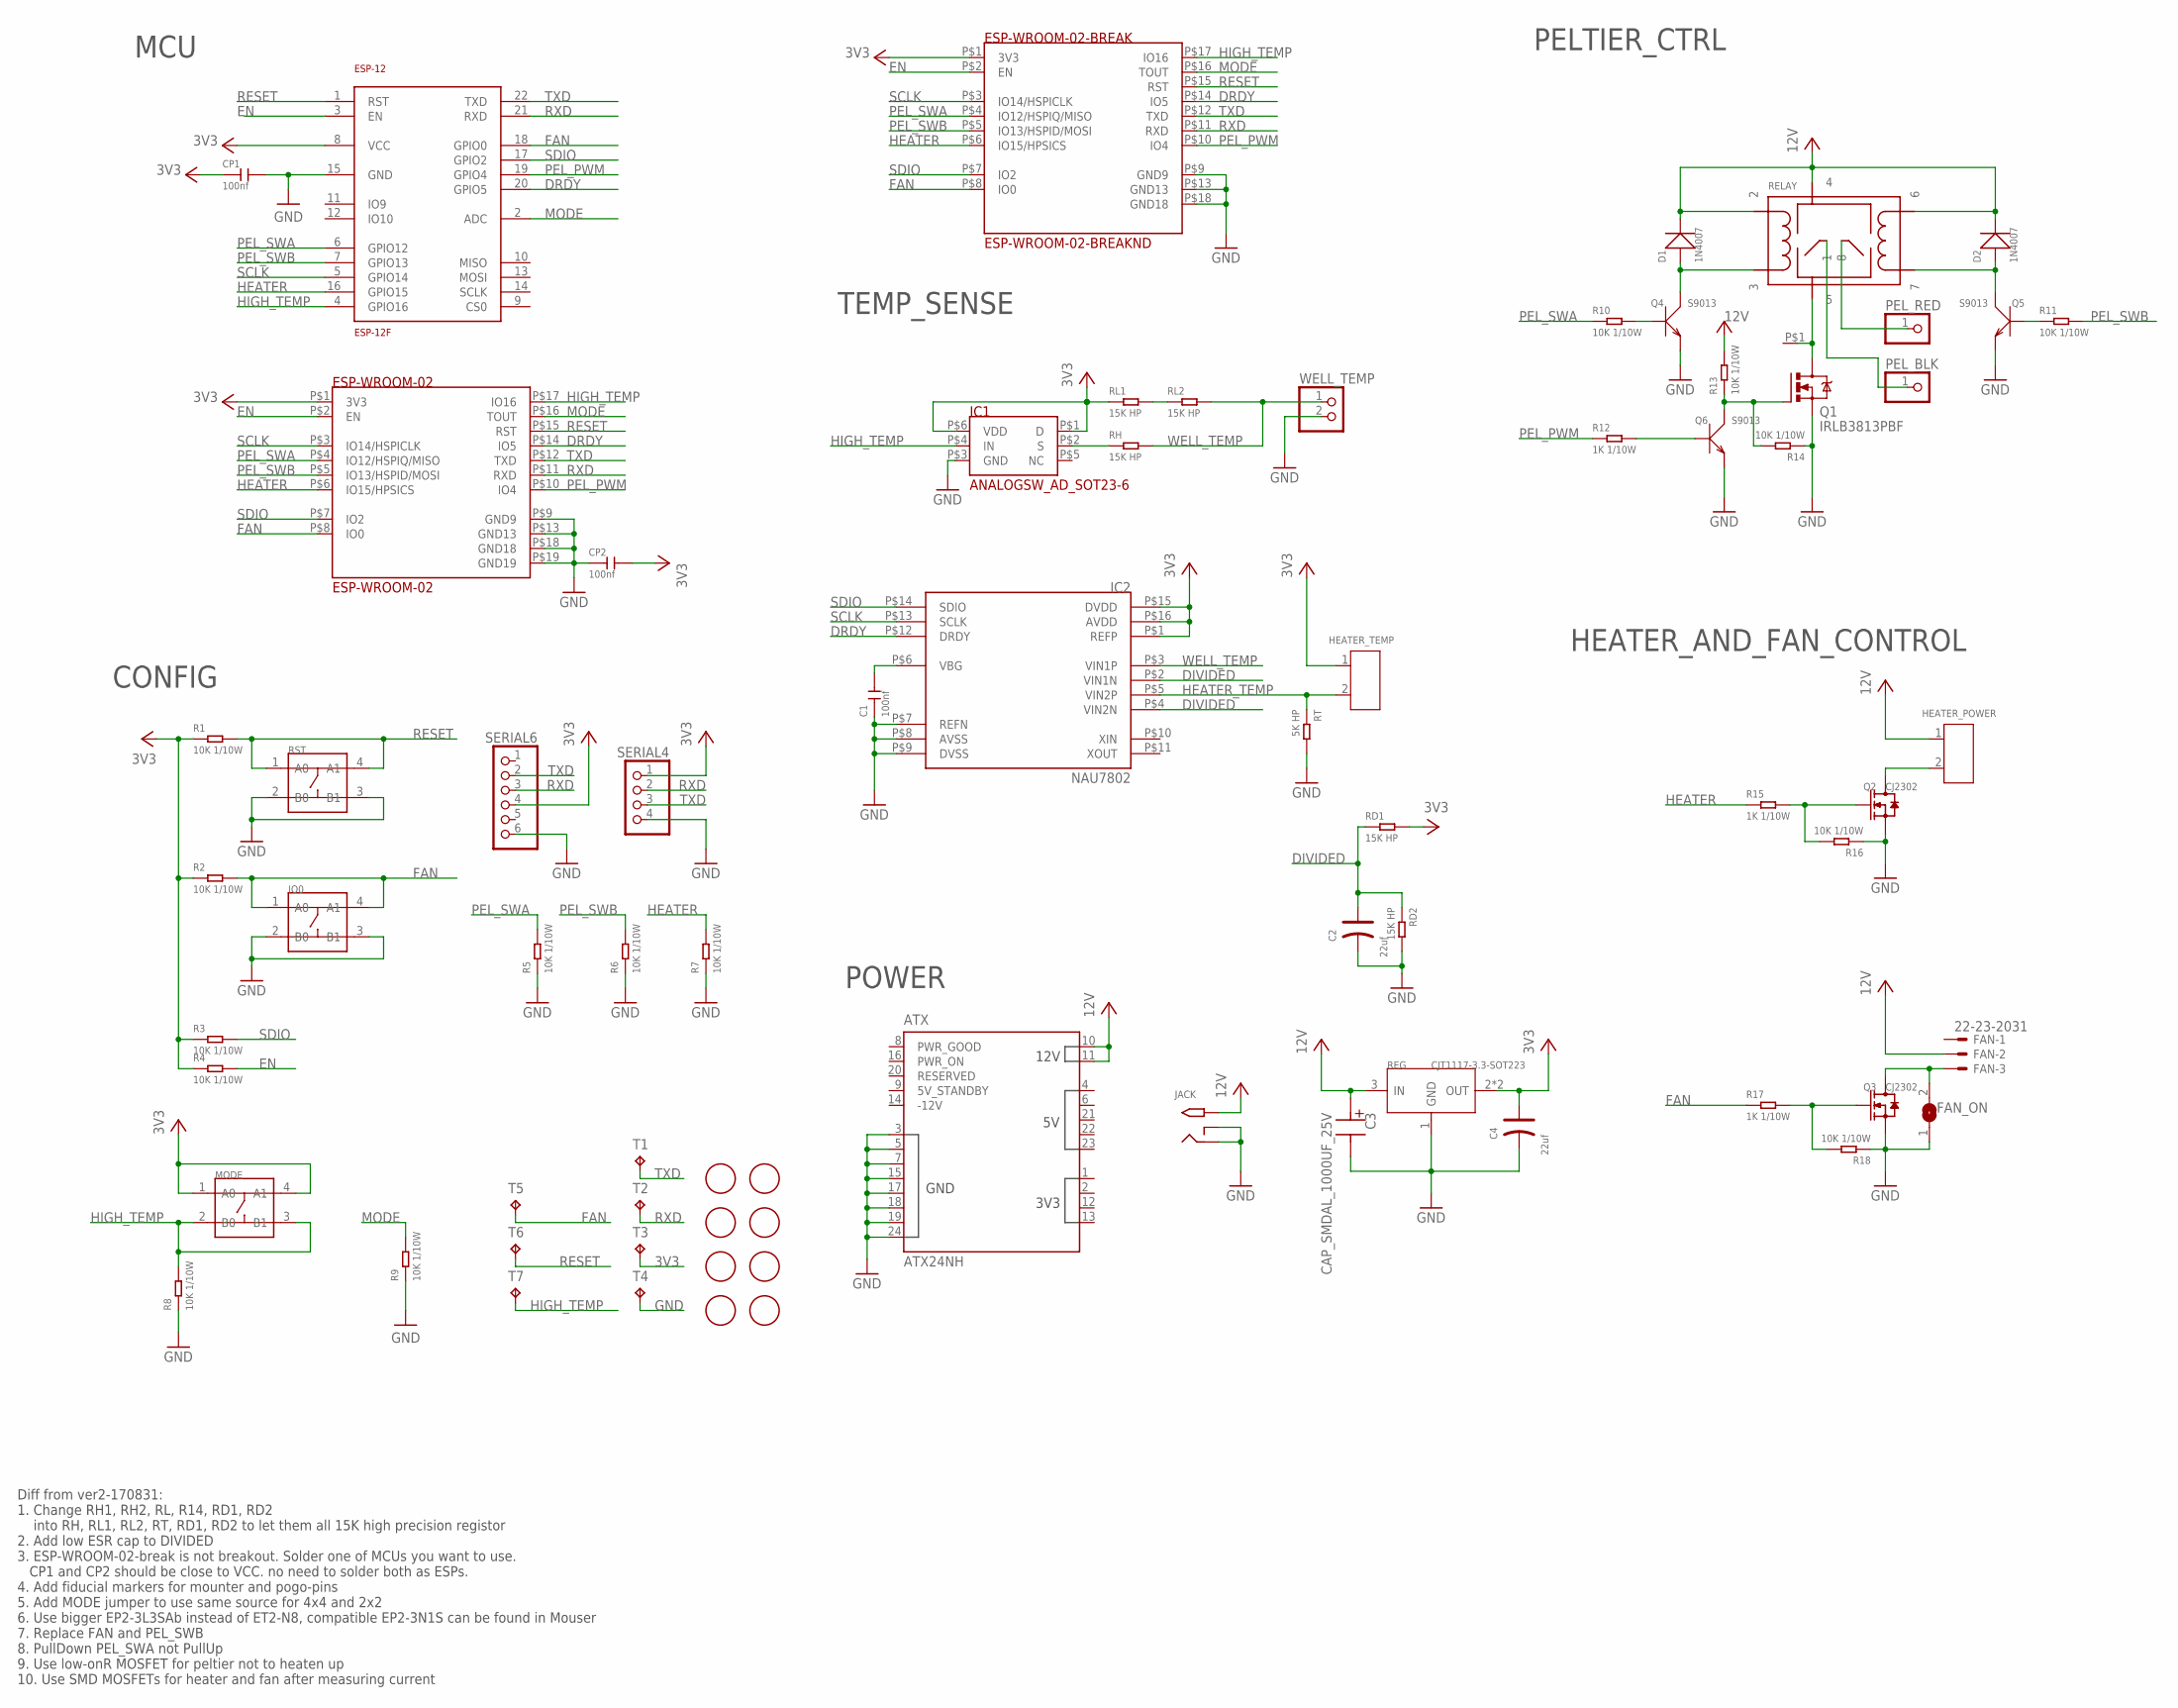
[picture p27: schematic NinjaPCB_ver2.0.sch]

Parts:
ATX: ATX24NH; ATX24
C1: 100nf; C0603
C2, C4: 22uf; AVX-B
C3: CAP_SMDAL_1000UF_25V; CAP_SMD_AL_D125
CP1, CP2: 100nf; C0603
D1, D2: 1N4007; DO-214AC
ESP-12: ESP-12F
ESP-WROOM-02: ESP-WROOM-02
ESP-WROOM-02-BREAK: ESP-WROOM-02-BREAKND; ESP-WROOM-02-BREAK-NODETAIL
FAN: 22-23-2031
FAN_ON: SJ
HEATER_POWER: SCREW-TERMINAL-GREEN(2P-3.5); H2-3.5-7.0X7.0MM
HEATER_TEMP: SCREW-TERMINAL-GREEN(2P-3.5); H2-3.5-7.0X7.0MM
HEATSINK: HEAT111PB015; HEAT11PB015
IC1: ANALOGSW_AD_SOT23-6; SOT-23-6
IC2: NAU7802; SOP-16
IO0: DIP-SWITCH-TACTILE-SPST-NO/TS-1109(4P-D6.0MM)'TS-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; SW4-6.0X6.0X5.0MM
JACK: 2.1MMJACKTHM-NOOUT; PJ-102A-NOOUT
MODE: DIP-SWITCH-TACTILE-SPST-NO/TS-1109(4P-D6.0MM)'TS-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; SW4-6.0X6.0X5.0MM
PEL_BLK: PINHD-1X1L; 1X01LONG
PEL_RED: PINHD-1X1L; 1X01LONG
Q1: IRLB3813PBF; TO220BV
Q2, Q3: CJ2302; SOT-23
Q4, Q5, Q6: S9013; SOT-23
R1, R2, R3, R4, R5, R6, R7, R8, R9, R10, R11, R13, R14, R16, R18: 10K 1/10W; R0603
R12, R15, R17: 1K 1/10W; R0603
RD1, RD2: 15K HP; R0603
REG: CJT1117-3.3-SOT223; SOT-223
RELAY: NEC-RELAY2EN2; NEC-EN2
RH: 15K HP; R0603
RL1, RL2: 15K HP; R0603
RST: DIP-SWITCH-TACTILE-SPST-NO/TS-1109(4P-D6.0MM)'TS-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; SW4-6.0X6.0X5.0MM
RT: 5K HP; R0603
SERIAL4: PINHD-1X4; 1X04
SERIAL6: PINHD-1X6; 1X06
T1, T2, T3, T4, T5, T6, T7: TPTP20R; TP20R
U$3, U$4, U$5, U$6, U$7, U$8, U$9, U$10: FIDUCIAL; FIDUCIAL_1MM
WELL_TEMP: PINHD-1X2; 1X02

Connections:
3V3: C4.+, CP1.1, CP2.2, ESP-12.8 (VCC), ESP-WROOM-02.P$1 (3V3), ESP-WROOM-02-BREAK.P$1 (3V3), HEATER_TEMP.1, IC1.P$1 (D), IC1.P$6 (VDD), IC2.P$1 (REFP), IC2.P$15 (DVDD), IC2.P$16 (AVDD), MODE.1 (A0), MODE.4 (A1), R1.1, R2.1, R3.1, R4.1, RD1.2, REG.2 (OUT), REG.TER (OUT), RL1.1, SERIAL4.1, SERIAL6.4, T3.TP
12V: ATX.10 (12V_10), ATX.11 (12V_11), C3.P$P, D1.2 (-), D2.2 (-), FAN.2, HEATER_POWER.1, JACK.TIP, R13.2, REG.3 (IN), RELAY.P$2 (2), RELAY.P$4 (4), RELAY.P$6 (6)
DIVIDED: C2.+, IC2.P$2 (VIN1N), IC2.P$4 (VIN2N), RD1.1, RD2.1
DRDY: ESP-12.20 (GPIO5), ESP-WROOM-02.P$14 (IO5), ESP-WROOM-02-BREAK.P$14 (IO5), IC2.P$12 (DRDY)
EN: ESP-12.3 (EN), ESP-WROOM-02.P$2 (EN), ESP-WROOM-02-BREAK.P$2 (EN), R4.2
FAN: ESP-12.18 (GPIO0), ESP-WROOM-02.P$8 (IO0), ESP-WROOM-02-BREAK.P$8 (IO0), IO0.1 (A0), IO0.4 (A1), R2.2, R17.1, T5.TP
GND: ATX.3 (GND3), ATX.5 (GND5), ATX.7 (GND7), ATX.15 (GND15), ATX.17 (GND17), ATX.18 (GND18), ATX.19 (GND19), ATX.24 (GND24), C1.1, C2.-, C3.P$M, C4.-, CP1.2, CP2.1, ESP-12.15 (GND), ESP-WROOM-02.P$9 (GND9), ESP-WROOM-02.P$13 (GND13), ESP-WROOM-02.P$18 (GND18), ESP-WROOM-02.P$19 (GND19), ESP-WROOM-02-BREAK.P$9 (GND9), ESP-WROOM-02-BREAK.P$13 (GND13), ESP-WROOM-02-BREAK.P$18 (GND18), FAN_ON.1, IC1.P$3 (GND), IC2.P$7 (REFN), IC2.P$8 (AVSS), IC2.P$9 (DVSS), IO0.2 (B0), IO0.3 (B1), JACK.RING, JACK.RING_SW, Q1.S, Q2.2 (S), Q3.2 (S), Q4.2 (E), Q5.2 (E), Q6.2 (E), R5.1, R6.1, R7.1, R8.1, R9.1, R14.1, R16.1, R18.1, RD2.2, REG.1 (GND), RST.2 (B0), RST.3 (B1), RT.2, SERIAL4.4, SERIAL6.6, T4.TP, WELL_TEMP.2
HEATER: ESP-12.16 (GPIO15), ESP-WROOM-02.P$6 (IO15/HPSICS), ESP-WROOM-02-BREAK.P$6 (IO15/HPSICS), R7.2, R15.1
HEATER_TEMP: HEATER_TEMP.2, IC2.P$5 (VIN2P), RT.1
HIGH_TEMP: ESP-12.4 (GPIO16), ESP-WROOM-02.P$17 (IO16), ESP-WROOM-02-BREAK.P$17 (IO16), IC1.P$4 (IN), MODE.2 (B0), MODE.3 (B1), R8.2, T7.TP
MODE: ESP-12.2 (ADC), ESP-WROOM-02.P$16 (TOUT), ESP-WROOM-02-BREAK.P$16 (TOUT), R9.2
unnamed: RL1.2, RL2.1
unnamed: HEATER_POWER.2, Q2.3 (D)
unnamed: HEATSINK.P$1, Q1.D, RELAY.P$5 (5)
unnamed: FAN.3, FAN_ON.2, Q3.3 (D)
unnamed: Q1.G, Q6.3 (C), R13.1, R14.2
unnamed: PEL_RED.1, RELAY.P$8 (8)
unnamed: PEL_BLK.1, RELAY.P$1 (1)
unnamed: Q3.1 (G), R17.2, R18.2
unnamed: IC1.P$2 (S), RH.1
unnamed: Q6.1 (B), R12.2
unnamed: Q2.1 (G), R15.2, R16.2
unnamed: D1.1 (+), Q4.3 (C), RELAY.P$3 (3)
unnamed: Q4.1 (B), R10.2
unnamed: Q5.1 (B), R11.1
unnamed: D2.1 (+), Q5.3 (C), RELAY.P$7 (7)
unnamed: C1.2, IC2.P$6 (VBG)
PEL_PWM: ESP-12.19 (GPIO4), ESP-WROOM-02.P$10 (IO4), ESP-WROOM-02-BREAK.P$10 (IO4), R12.1
PEL_SWA: ESP-12.6 (GPIO12), ESP-WROOM-02.P$4 (IO12/HSPIQ/MISO), ESP-WROOM-02-BREAK.P$4 (IO12/HSPIQ/MISO), R5.2, R10.1
PEL_SWB: ESP-12.7 (GPIO13), ESP-WROOM-02.P$5 (IO13/HSPID/MOSI), ESP-WROOM-02-BREAK.P$5 (IO13/HSPID/MOSI), R6.2, R11.2
RESET: ESP-12.1 (RST), ESP-WROOM-02.P$15 (RST), ESP-WROOM-02-BREAK.P$15 (RST), R1.2, RST.1 (A0), RST.4 (A1), T6.TP
RXD: ESP-12.21 (RXD), ESP-WROOM-02.P$11 (RXD), ESP-WROOM-02-BREAK.P$11 (RXD), SERIAL4.2, SERIAL6.3, T2.TP
SCLK: ESP-12.5 (GPIO14), ESP-WROOM-02.P$3 (IO14/HSPICLK), ESP-WROOM-02-BREAK.P$3 (IO14/HSPICLK), IC2.P$13 (SCLK)
SDIO: ESP-12.17 (GPIO2), ESP-WROOM-02.P$7 (IO2), ESP-WROOM-02-BREAK.P$7 (IO2), IC2.P$14 (SDIO), R3.2
TXD: ESP-12.22 (TXD), ESP-WROOM-02.P$12 (TXD), ESP-WROOM-02-BREAK.P$12 (TXD), SERIAL4.3, SERIAL6.2, T1.TP
WELL_TEMP: IC2.P$3 (VIN1P), RH.2, RL2.2, WELL_TEMP.1

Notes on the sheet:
TEMP_SENSE
HEATER_AND_FAN_CONTROL
PELTIER_CTRL
MCU
POWER
Diff from ver2-170831: 1. Change RH1, RH2, RL, R14, RD1, RD2 into RH, RL1, RL2, RT, RD1, RD2 to let them all 15K high precision registor 2. Add low ESR cap to DIVIDED 3. ESP-WROOM-02-break is not breakout. Solder one of MCUs you want to use. CP1 and CP2 should be close to VCC. no need to solder bot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
CONFIG

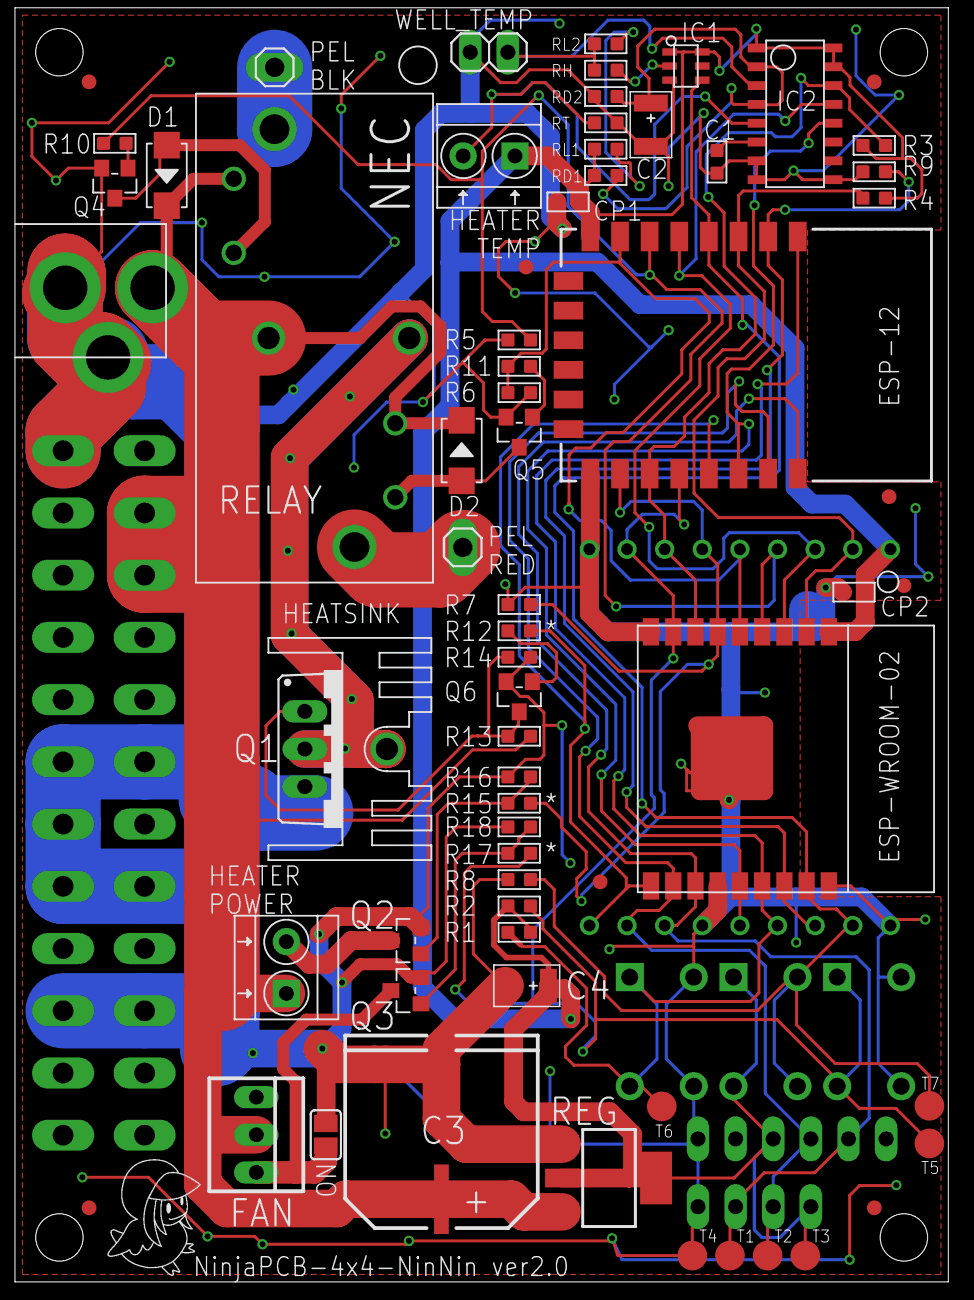
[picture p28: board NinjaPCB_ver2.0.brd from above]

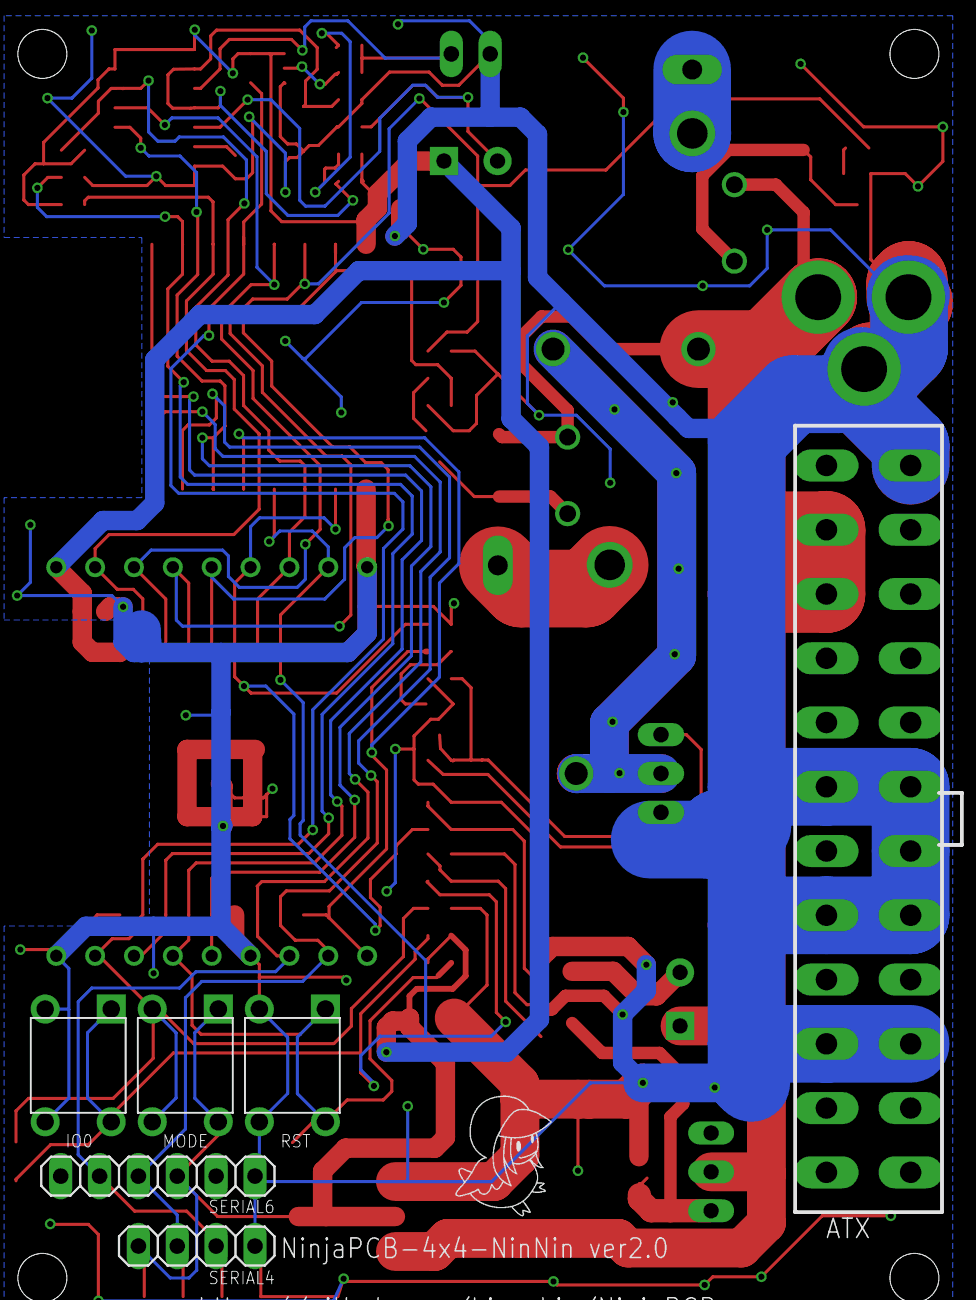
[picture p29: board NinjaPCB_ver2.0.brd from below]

Board: 2 copper layers, 77 parts (7 on the bottom side), 36 nets.

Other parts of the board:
U$1, U$2: TORI_0.25

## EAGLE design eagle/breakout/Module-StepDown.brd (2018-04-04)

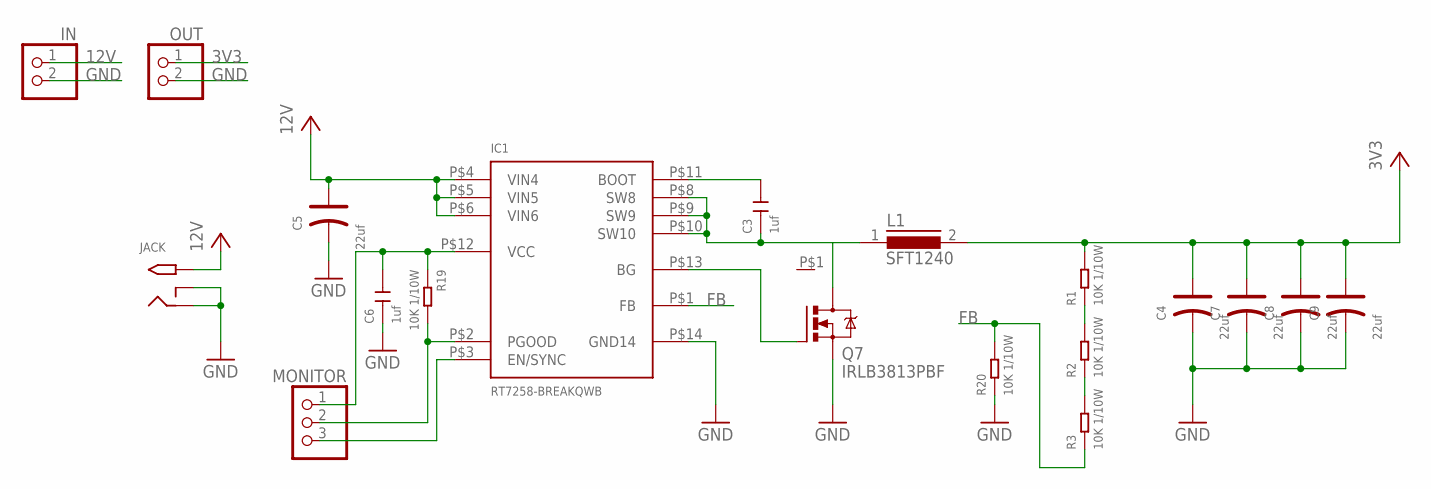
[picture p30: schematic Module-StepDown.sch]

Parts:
C3, C6: 1uf; C0603
C4, C5, C7, C8, C9: 22uf; AVX-B
HEATSINK1: HEAT111PB015; HEAT11PB015
IC1: RT7258-BREAKQWB; RT7258GQW-BREAK
IN: PINHD-1X2; 1X02
JACK: 2.1MMJACKTHM-NOOUT; PJ-102A-NOOUT
L1: SFT1240
MONITOR: PINHD-1X3; 1X03
OUT: PINHD-1X2; 1X02
Q7: IRLB3813PBF; TO220BV
R1, R2, R3, R19, R20: 10K 1/10W; R0603

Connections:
3V3: C4.+, C7.+, C8.+, C9.+, L1.2, OUT.1, R1.2
12V: C5.+, IC1.P$4 (VIN4), IC1.P$5 (VIN5), IC1.P$6 (VIN6), IN.1, JACK.TIP
EN/SYNC: IC1.P$3 (EN/SYNC), MONITOR.3
FB: IC1.P$1 (FB), R3.1, R20.2
GND: C4.-, C5.-, C6.1, C7.-, C8.-, C9.-, IC1.P$14 (GND14), IN.2, JACK.RING, JACK.RING_SW, OUT.2, Q7.S, R20.1
unnamed: R2.1, R3.2
unnamed: R1.1, R2.2
unnamed: C3.2, IC1.P$11 (BOOT)
unnamed: IC1.P$13 (BG), Q7.G
PGOOD: IC1.P$2 (PGOOD), MONITOR.2, R19.2
SW: C3.1, IC1.P$8 (SW8), IC1.P$9 (SW9), IC1.P$10 (SW10), L1.1, Q7.D
VCC: C6.2, IC1.P$12 (VCC), MONITOR.1, R19.1

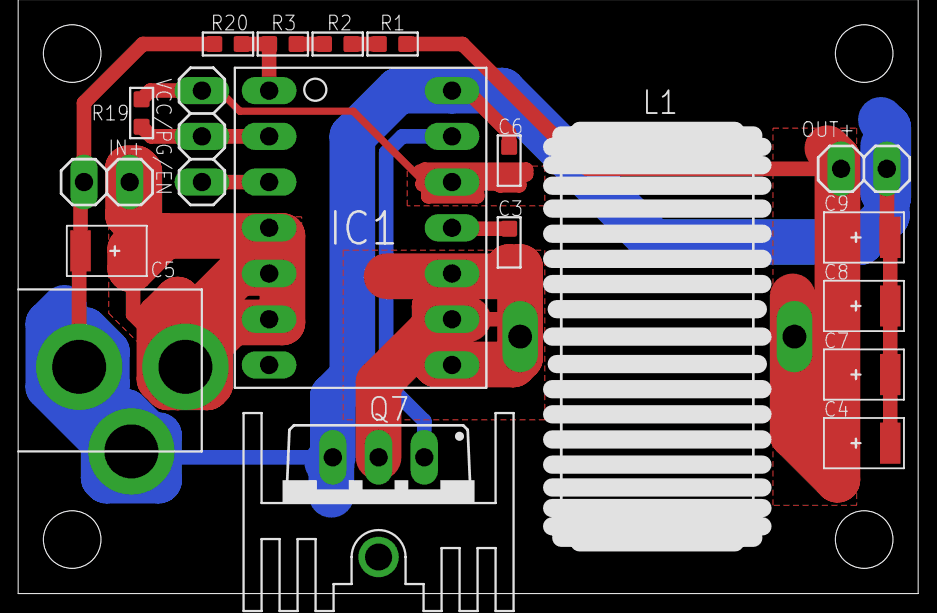
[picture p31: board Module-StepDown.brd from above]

Board: 2 copper layers, 20 parts (0 on the bottom side), 12 nets.

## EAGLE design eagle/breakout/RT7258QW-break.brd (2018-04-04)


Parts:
JP1, JP2: PINHD-1X7; 1X07
U$1: RT7258QW; RT7258GQW

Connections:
1: JP1.1, U$1.P$1 (FB)
2: JP1.2, U$1.P$2 (PGOOD)
3: JP1.3, U$1.P$3 (EN/SYNC)
4: JP1.4, U$1.P$4 (VIN4)
5: JP1.5, U$1.P$5 (VIN5)
6: JP1.6, U$1.P$6 (VIN6)
7: JP1.7
8: JP2.7, U$1.P$8 (SW8)
9: JP2.6, U$1.P$9 (SW9)
10: JP2.5, U$1.P$10 (SW10)
11: JP2.4, U$1.P$11 (BOOT)
12: JP2.3, U$1.P$12 (VCC)
13: JP2.2, U$1.P$13 (BG)
14: JP2.1, U$1.P$14 (GND14), U$1.P$15 (GND15)


Board: 2 copper layers, 3 parts (0 on the bottom side), 13 nets.

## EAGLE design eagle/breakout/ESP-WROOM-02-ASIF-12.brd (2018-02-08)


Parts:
EN-PUP: 10K; R0805
IO0-PDN, IO0-PUP, IO2-PUP, IO15-PDN: SJ
LEFT: PINHD-1X11OCT; 1X11OCT
RIGHT: PINHD-1X11OCT; 1X11OCT
RST-PUP: 10K; R0805
U1: ESP-WROOM-02

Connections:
3V3: EN-PUP.2, IO0-PUP.1, IO2-PUP.1, LEFT.8, RST-PUP.2, U1.P$1 (3V3)
EN: EN-PUP.1, LEFT.3, U1.P$2 (EN)
GND: IO0-PDN.1, IO15-PDN.1, RIGHT.8, U1.P$9 (GND9), U1.P$13 (GND13), U1.P$18 (GND18), U1.P$19 (GND19)
IO0: IO0-PDN.2, IO0-PUP.2, RIGHT.5, U1.P$8 (IO0)
IO2: IO2-PUP.2, RIGHT.6, U1.P$7 (IO2)
IO4: RIGHT.4, U1.P$10 (IO4)
IO5: RIGHT.3, U1.P$14 (IO5)
IO12: LEFT.6, U1.P$4 (IO12/HSPIQ/MISO)
IO13: LEFT.7, U1.P$5 (IO13/HSPID/MOSI)
IO14: LEFT.5, U1.P$3 (IO14/HSPICLK)
IO15: IO15-PDN.2, RIGHT.7, U1.P$6 (IO15/HPSICS)
IO16: LEFT.4, U1.P$17 (IO16)
NC1: LEFT.9
NC2: LEFT.10
NC3: LEFT.11
NC4: RIGHT.11
NC5: RIGHT.10
NC6: RIGHT.9
RST: LEFT.1, RST-PUP.1, U1.P$15 (RST)
RXD: RIGHT.2, U1.P$11 (RXD)
TOUT: LEFT.2, U1.P$16 (TOUT)
TXD: RIGHT.1, U1.P$12 (TXD)



Board: 2 copper layers, 26.0 x 28.6 mm, 9 parts (6 on the bottom side), 16 nets.

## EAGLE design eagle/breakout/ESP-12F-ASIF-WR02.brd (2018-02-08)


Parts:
EN-PUP: 10K; R0805
IO0-PDN, IO0-PUP, IO2-PUP, IO15-PDN: SJ
JP1: PINHD-1X6; 1X06
LEFT: PINHD-1X9; 1X09
RIGHT: PINHD-1X9; 1X09
RST-PUP: 10K; R0805
U1: ESP-12F

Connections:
3V3: EN-PUP.2, IO0-PUP.1, IO2-PUP.1, LEFT.1, RST-PUP.2, U1.8 (VCC)
CS0: JP1.1, U1.9 (CS0)
EN: EN-PUP.1, LEFT.2, U1.3 (EN)
GND: IO0-PDN.1, IO15-PDN.1, LEFT.9, RIGHT.1, RIGHT.6, U1.15 (GND)
IO0: IO0-PDN.2, IO0-PUP.2, LEFT.8, U1.18 (GPIO0)
IO2: IO2-PUP.2, LEFT.7, U1.17 (GPIO2)
IO4: RIGHT.9, U1.19 (GPIO4)
IO5: RIGHT.5, U1.20 (GPIO5)
IO9: JP1.3, U1.11 (IO9)
IO10: JP1.4, U1.12 (IO10)
IO12: LEFT.4, U1.6 (GPIO12)
IO13: LEFT.5, U1.7 (GPIO13)
IO14: LEFT.3, U1.5 (GPIO14)
IO15: IO15-PDN.2, LEFT.6, U1.16 (GPIO15)
IO16: RIGHT.2, U1.4 (GPIO16)
MISO: JP1.2, U1.10 (MISO)
MOSI: JP1.5, U1.13 (MOSI)
RST: RIGHT.4, RST-PUP.1, U1.1 (RST)
RXD: RIGHT.8, U1.21 (RXD)
SCLK: JP1.6, U1.14 (SCLK)
TOUT: RIGHT.3, U1.2 (ADC)
TXD: RIGHT.7, U1.22 (TXD)



Board: 2 copper layers, 29.0 x 24.0 mm, 10 parts (6 on the bottom side), 22 nets.

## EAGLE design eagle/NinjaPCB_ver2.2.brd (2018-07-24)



Board: 2 copper layers, 79.0 x 73.0 mm, 74 parts (8 on the bottom side), 36 nets.

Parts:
ATX: ATX24NH; ATX24
C1, C5: 100nf; C0603
C2, C4: 22uf; AVX-B
C3: CAP_SMDAL_1000UF_25V; CAP_SMD_AL_D125
CP1, CP2: 100nf; C0603
D1, D2: 1N4007; DO-214AC
DIN4: DIN4
ESP1: ESP-12F
ESP2: ESP-WROOM-02
ESP3: ESP-WROOM-02-BREAKND; ESP-WROOM-02-BREAK-NODETAIL
FAN: 22-23-2031
HEATER_POWER: H2-3.5-7.0X7.0MM
HEATER_TEMP: H2-3.5-7.0X7.0MM
HEATSINK: HEAT111PB015; HEAT11PB015
IC1: ANALOGSW_AD_SOT23-5; SOT23-5
IC2: NAU7802; SOP-16
IO0: 1X02
JACK: 2.1MMJACKTHM-NOOUT; PJ-102A-NOOUT
MODE: SW4-6.0X6.0X5.0MM
PELTIER: H2-3.5-7.0X7.0MM
Q1: IRLB3813PBF; TO220BV
Q2, Q3: CJ2302; SOT-23
Q4, Q5, Q6: S9013; SOT-23
R1, R2, R3, R4, R5, R6, R7, R8, R10, R11, R12, R15, R16, R18, R20: 10K 1/10W; R0603
R9: 100K 1/10W; R0603
R13, R17, R19, R22: 1K 1/10W; R0603
R14, R21: 0R; R0603
RD1, RD2: 15K HP; R0603
REG: CJT1117-3.3-SOT223; SOT-223
RELAY: NEC-RELAY2EP2; NEC-EP2
RESET: 1X02
RH: 15K HP; R0603
RL1, RL2: 15K HP; R0603
RST: SW4-6.0X6.0X5.0MM
RT: 4.99K HP; R0603
SERIAL4: 1X04
SERIAL6: 1X06
U$1, U$2: OSHW_5MM
U$3, U$4, U$5, U$7, U$8, U$9, U$10: FIDUCIAL; FIDUCIAL_1MM
WELL_TEMP: 1X02/90

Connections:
3V3: C4.+, CP1.1, CP2.2, ESP1.8, ESP2.P$1, ESP3.P$1, HEATER_TEMP.1, IC1.1, IC1.6, IC2.P$1, IC2.P$15, IC2.P$16, MODE.1, MODE.4, R1.1, R2.1, R3.1, R4.1, R9.2, R22.2, RD1.2, REG.2, REG.TER, RL1.1
12V: ATX.10, ATX.11, C3.P$P, D1.2, D2.2, DIN4.P$1, DIN4.P$2, FAN.2, HEATER_POWER.1, JACK.TIP, R15.2, REG.3, RELAY.P$2, RELAY.P$4, RELAY.P$6
BLK: PELTIER.2, RELAY.P$1
DIVIDED: C2.+, IC2.P$2, IC2.P$4, RD1.1, RD2.1
DRDY: ESP1.20, ESP2.P$14, ESP3.P$14, IC2.P$12
EN: C5.2, ESP1.3, ESP2.P$2, ESP3.P$2, R4.2, R22.1
FAN: ESP1.18, ESP2.P$8, ESP3.P$8, IO0.1, R2.2, R19.1
GND: ATX.3, ATX.5, ATX.7, ATX.15, ATX.16, ATX.17, ATX.18, ATX.19, ATX.24, C1.1, C2.-, C3.P$M, C4.-, C5.1, CP1.2, CP2.1, DIN4.P$3, DIN4.P$4, DIN4.P$6, DIN4.P$7, DIN4.P$8, DIN4.P$9, ESP1.15, ESP2.P$9, ESP2.P$13, ESP2.P$18, ESP2.P$19, ESP3.P$9, ESP3.P$13, ESP3.P$18, IC1.3, IC2.P$7, IC2.P$8, IC2.P$9, IO0.2, JACK.RING, JACK.RING_SW, Q1.S, Q2.2, Q3.2, Q4.2, Q5.2, Q6.2, R5.1, R6.1, R7.1, R8.1, R10.2, R16.1, R18.1, R20.1, R21.1, RD2.2, REG.1, RST.2, RST.3, RT.2, SERIAL4.4, SERIAL6.6, WELL_TEMP.2
HEATER: ESP1.16, ESP2.P$6, ESP3.P$6, R7.2, R17.1
HEATER_TEMP: HEATER_TEMP.2, IC2.P$5, RT.1
HIGH_TEMP: ESP1.4, ESP2.P$17, ESP3.P$17, IC1.4, MODE.2, MODE.3, R8.2, RESET.2
unnamed: RL1.2, RL2.1
unnamed: HEATER_POWER.2, Q2.3
unnamed: HEATSINK.P$1, Q1.D, RELAY.P$5
unnamed: FAN.3, Q3.3, R21.2
unnamed: Q1.G, Q6.3, R14.2, R15.1, R16.2
unnamed: Q3.1, R19.2, R20.2
unnamed: IC1.2, RH.1
unnamed: Q6.1, R13.2, R14.1
unnamed: Q2.1, R17.2, R18.2
unnamed: D1.1, Q4.3, RELAY.P$3
unnamed: Q4.1, R11.2
unnamed: Q5.1, R12.1
unnamed: D2.1, Q5.3, RELAY.P$7
unnamed: C1.2, IC2.P$6
PEL_PWM: ESP1.19, ESP2.P$10, ESP3.P$10, R13.1
PEL_SWA: ESP1.6, ESP2.P$4, ESP3.P$4, R5.2, R11.1
PEL_SWB: ESP1.7, ESP2.P$5, ESP3.P$5, R6.2, R12.2
RED: PELTIER.1, RELAY.P$8
RESET: ESP1.1, ESP2.P$15, ESP3.P$15, R1.2, RESET.1, RST.1, RST.4
RXD: ESP1.21, ESP2.P$11, ESP3.P$11, SERIAL4.2, SERIAL6.3
SCLK: ESP1.5, ESP2.P$3, ESP3.P$3, IC2.P$13
SDIO: ESP1.17, ESP2.P$7, ESP3.P$7, IC2.P$14, R3.2
TOUT: ESP1.2, ESP2.P$16, ESP3.P$16, R9.1, R10.1
TXD: ESP1.22, ESP2.P$12, ESP3.P$12, SERIAL4.3, SERIAL6.2
WELL_TEMP: IC2.P$3, RH.2, RL2.2, WELL_TEMP.1

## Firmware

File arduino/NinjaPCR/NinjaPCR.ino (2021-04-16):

/*
 *  openpcr.pde - OpenPCR control software.
 *  Copyright (C) 2010-2012 Josh Perfetto. All Rights Reserved.
 *
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
 *  You should have received a copy of the GNU General Public License along with
 *  the OpenPCR control software.  If not, see <http://www.gnu.org/licenses/>.
 */

#include <LiquidCrystal.h>
#include <EEPROM.h>

#include "pcr_includes.h"
#include "adc.h"
#include "thermocycler.h"
#include "thermistors.h"
#include <ESP8266WiFi.h>
#include <ESP8266WebServer.h>
#include <ESP8266WiFiMulti.h>
#include <ESP8266HTTPClient.h>
#include "serialcontrol_chrome.h"
#include "wifi_communicator.h"


#ifdef DEBUG
String debug = "NINJAPCR_DEBUG";
#endif
#ifdef DEBUG_NETWORK
String debugNetwork = "NINJAPCR_DEBUG_NETWORK";
#endif
#ifdef DEBUG_ADC
String debugADC = "NINJAPCR_DEBUG_ADC";
#endif
#ifdef DEBUG_ESP_CORE
String debugEspCore = "NINJAPCR_DEBUG_ESP_CORE";
#endif
#ifdef DEBUG_ESP_SSL
String debugEspSSL = "NINJAPCR_DEBUG_ESP_SSL";
#endif
#ifdef DEBUG_ESP_WIFI
String debugEspWiFi = "NINJAPCR_DEBUG_ESP_WIFI";
#endif
#ifdef DEBUG_ESP_HTTP_CLIENT
String debugEspHTTPClient = "NINJAPCR_DEBUG_ESP_HTTP_CLIENT";
#endif
#ifdef DEBUG_ESP_HTTP_UPDATE
String debugEspHTTPUpdate = "NINJAPCR_DEBUG_ESP_HTTP_UPDATE";
#endif
#ifdef DEBUG_ESP_HTTP_SERVER
String debugEspHTTPServer = "NINJAPCR_DEBUG_ESP_HTTP_SERVER";
#endif
#ifdef DEBUG_ESP_UPDATER
String debugEspUpdater = "NINJAPCR_DEBUG_ESP_UPDATER";
#endif
#ifdef DEBUG_ESP_OTA
String debugEspOTA = "NINJAPCR_DEBUG_ESP_OTA";
#endif

String versionDescription = FIRMWARE_VERSION_DESCRIPTION; // NEVER REMOVE THIS LINE!

Thermocycler* gpThermocycler = NULL;
WifiCommunicator *wifi = NULL;

boolean isInitialStart() {
    for (int i = 0; i < 50; i++) {
        if (EEPROM.read(i) != 0xFF)
            return false;
    }
    return true;
}

const SPIDTuning LID_PID_GAIN_SCHEDULE2[] =
    {
    //maxTemp, kP, kI, kD
                { 70, 40, 0.15, 60 },
                { 200, 80, 1.1, 10 } };

bool isApMode = false;

void setup() {
    Serial.begin(BAUD_RATE);
    pinMode(PIN_WIFI_MODE, INPUT);
    delay(100);
    isApMode = (digitalRead(PIN_WIFI_MODE)==VALUE_WIFI_MODE_AP);
    delay(250);
    PCR_DEBUG("NinjaPCR ver. ");
    PCR_DEBUG_LINE(OPENPCR_FIRMWARE_VERSION_STRING);
    initHardware();
    EEPROM.begin(1024);

    PCR_DEBUG("PIN_WIFI_MODE=");
    PCR_DEBUG_LINE(isApMode);
    if (isApMode) {
        PCR_DEBUG_LINE("AP mode");
        startWiFiAPMode();

        // Init AP mode
        setup_normal();
        wifi = new WifiCommunicator(wifi_receive, wifi_send);
        gpThermocycler->SetCommunicator(wifi);
    }
    else {
        PCR_DEBUG_LINE("HTTP Server mode");
  #ifdef USE_FAN
    digitalWrite(PIN_FAN, PIN_FAN_VALUE_ON);
  #endif
        startWiFiHTTPServerMode();
        setup_normal();
        wifi = new WifiCommunicator(wifi_receive, wifi_send);
        gpThermocycler->SetCommunicator(wifi);
    }
}

void setup_normal() {

#ifdef USE_STATUS_PINS
    pinMode(PIN_STATUS_A,OUTPUT);
    pinMode(PIN_STATUS_B,OUTPUT);
    digitalWrite(PIN_STATUS_A,LOW);
    digitalWrite(PIN_STATUS_B,LOW);
#endif /* USE_STATUS_PINS */

    //init factory settings
    /*
    if (isInitialStart()) {
        EEPROM.write(0, 100); // set contrast to 100
    }
    */
    //restart detection

#ifdef USE_WIFI
    //TODO EEPROM
    boolean restarted = false;
#else
    boolean restarted = !(MCUSR & 1);
    MCUSR &= 0xFE;
#endif /* USE_WIFI */

#ifdef USE_STATUS_PINS
    digitalWrite(PIN_STATUS_A, HIGH);
#endif /* USE_STATUS_PINS */
    gpThermocycler = new Thermocycler(restarted);
}

bool isSerialConnected = false;
bool initDone = false;

int sec = 0;
bool finishSent = false;
void loop() {
    unsigned long startMillis;
    unsigned long elapsed;

    /*
    if (isApMode) {
        delay(100);
        loopWiFiAP();
        return;
    }
    */

    startMillis = millis();
    /*
     * Pause heating & cooling units while processing HTTP requests
     * to avoid overheating
     */
    gpThermocycler->PauseHeatUnits();
    if (isWiFiConnected()) {
        loopWiFiHTTPServer();
    }

    elapsed = millis() - startMillis;
    if (elapsed<0 || elapsed > INTERVAL_MSEC) {
        elapsed = 0;
    }
    double powerOutputRatio = (double)INTERVAL_MSEC/(double)max(INTERVAL_MSEC/2, INTERVAL_MSEC-elapsed);
    PCR_DEBUG("powerOutputRatio=");
    PCR_DEBUG_LINE(powerOutputRatio);
    gpThermocycler->SetPowerOutputRatio(powerOutputRatio);
    gpThermocycler->Loop();

    if (gpThermocycler->GetProgramState() == Thermocycler::ProgramState::EComplete) {
        PCR_DEBUG_LINE("COMPLETE");
        if (!finishSent) {
            // TODO call IFTTT API if needed
            finishSent = true;
        }
    }
    delay(INTERVAL_MSEC-elapsed);
}

bool startLamp = false;
void checkSerialConnection() {
    Serial.print("\n");
#ifdef USE_STATUS_PINS
    digitalWrite(PIN_STATUS_A, (startLamp)?HIGH:LOW);
#endif /* USE_STATUS_PINS */
    startLamp = !startLamp;
    unsigned long timeStart = millis();
    while (millis() < timeStart + INTERVAL_MSEC) {
        while (Serial.available()) {
            char ch = Serial.read();
            if (ch == 'a' && !isSerialConnected) {
#ifdef USE_STATUS_PINS
                digitalWrite(PIN_STATUS_A, LOW);
#endif /* USE_STATUS_PINS */
                isSerialConnected = true;
            }
        }
    }
}

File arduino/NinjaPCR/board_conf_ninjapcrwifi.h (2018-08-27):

#ifndef ___BOARD_CONF_NINJAPCR___
#define ___BOARD_CONF_NINJAPCR___

#define BAUD_RATE 115200
/* Board Config */
#define USE_ESP8266

/* ADC (NAU7802 or MCP3554) */
#define USE_ADC_NAU7802
//#define USE_ADC_MCP3554
#define TEHRMISTORS_NINJAPCR

// Thermistor value is measured by 2 ranges, switched by analog switch
#define THERMISTOR_2_RANGES
#define PIN_THERMISTOR_RANGE_SWITCH 16 /* Analog switch */

#define USE_WIFI /* Use WiFi functionalities */
#define PIN_WIFI_MODE 16 /* Digitai input pin to switch AP (pairing) mode and Normal mode  */
#define VALUE_WIFI_MODE_AP HIGH /* Start with AP (pairing) mode if value of PIN_WIFI_MODE agrees with this.  */
// #define USE_LCD /* Use display */
// #define USE_STATUS_PINS /* Use status LEDs */
// #define DEBUG_DISPLAY

/* Use LCD */

/* LCD Pins (Dummy) */
#define PIN_LCD_RS 6
#define PIN_LCD_ENABLE 7
#define PIN_LCD_D4 8
//#define PIN_LCD_D5 A5
#define PIN_LCD_D5 5 // TMP
#define PIN_LCD_D6 16
#define PIN_LCD_D7 17
#define PIN_LCD_CONTRAST 5

/* Lid */
#define PIN_LID_THERMISTOR_AIN 1 // TODO Use TOUT
#define PIN_LID_PWM 15 // PWM is available
// #define PIN_LID_PWM_ACTIVE_LOW
#define USE_ESP8266

/* Well */
#ifdef  USE_ADC_NAU7802
#define PIN_WELL_INA 12
#endif
#ifdef USE_ADC_MCP3554
#define PIN_WELL_INA 12
#endif
#define PIN_WELL_INB 13
#define PIN_WELL_PWM 4
#define PIN_WELL_PWM_ACTIVE_LOW
#define PIN_WELL_HIGH_TEMP 16

/* Fan */
#define USE_FAN
#define PIN_FAN 0
#define PIN_FAN_VALUE_ON HIGH
#define PIN_FAN_VALUE_OFF LOW
/* Suppress frequent switching of relay */
#define SUPPRESS_PELTIER_SWITCHING
/*
 * Define on/off logic values according to
 * polarity of transistors for the relay
 */
#define PIN_WELL_VALUE_ON LOW
#define PIN_WELL_VALUE_OFF HIGH

/* SPI */
#define PIN_WELL_MCP3554_DATAOUT 13//MOSI (Not used)
#define PIN_WELL_MCP3554_DATAIN  12//MISO
#define PIN_WELL_MCP3554_SPICLOCK  14//sck
#define PIN_WELL_MCP3554_SLAVESELECT 5//ss


/* SPI */
#ifdef USE_ADC_MCP3554
#define PIN_WELL_MCP3554_DATAOUT 13//MOSI (Not used)
#define PIN_WELL_MCP3554_DATAIN  12//MISO
#define PIN_WELL_MCP3554_SPICLOCK  14//sck
#define PIN_WELL_MCP3554_SLAVESELECT 5//ss
#endif /* USE_ADC_MCP3554 */

#ifdef USE_ADC_NAU7802
#define PIN_WELL_NAU7802_SCL 14
#define PIN_WELL_NAU7802_SDA 2
#define PIN_WELL_NAU7802_RDY 5
#endif /* USE_ADC_NAU7802 */

#define MIN_PELTIER_PWM -1023
#define MAX_PELTIER_PWM 1023

#define MAX_LID_PWM 1023
#define MIN_LID_PWM 0


#endif /* ___BOARD_CONF_NINJAPCR___ */

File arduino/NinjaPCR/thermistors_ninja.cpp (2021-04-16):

/*
 *  program.cpp - OpenPCR control software.
 *  Copyright (C) 2010-2012 Josh Perfetto. All Rights Reserved.
 *
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
 *  You should have received a copy of the GNU General Public License along with
 *  the OpenPCR control software.  If not, see <http://www.gnu.org/licenses/>.
 */

#include "pcr_includes.h"
#include "thermistors.h"
#include "adc.h"
#include <Arduino.h>

#ifdef TEHRMISTORS_NINJAPCR

#define THERMISTOR_BASE_TEMP 25.0

#define KELVIN 273.15

// Well Thermistor
#define B_CONST_25_50 4250
#define B_CONST_25_85 4311
#define B_CONST_25_100 4334
#define R_0_WELL 100.0

/*
// 103-JT-025
#define B_CONST_HEATER 3435
#define R_0_HEATER 100.0
*/



// 104-JT-025
#define B_CONST_HEATER 4390
#define R_0_HEATER 100.0 

// Counter resistors
#define R_LOW_TEMP 30.0 // Well low mode
#define R_HIGH_TEMP 10 // Well high mode (30x3)
#define R_HEATER 4.99 // Heater

#define HIGH_LOW_SWITCHING_TEMP 54
//#define PRINT_DEBUG_CHART

static float INVERSE_BASE_TEMP = 1.0 / (THERMISTOR_BASE_TEMP + KELVIN);

double voltageToTemp (double voltageRatio, float resistance, float b_constant, float r0) {
    double thermistorR = resistance * voltageRatio / (1.0 - voltageRatio);
    return (1 / ((log(thermistorR / r0) / b_constant) + INVERSE_BASE_TEMP))  - KELVIN;
}
double tempToVoltageRatio (double tempCelsius, double resistance, double bConst, double r0) {
    double thermistorR = r0 * exp(bConst * (1/(tempCelsius+KELVIN) - 1/(THERMISTOR_BASE_TEMP+KELVIN)));
    return thermistorR/(thermistorR+ resistance);
}

////////////////////////////////////////////////////////////////////
// Class CLidThermistor
static double SWITCHING_VOLTAGE_50_LID = 0;
static double SWITCHING_VOLTAGE_85_LID = 0;

CLidThermistor::CLidThermistor() :
        iTemp(0.0) {
    PCR_DEBUG_LINE("CLidThermistor");

    SWITCHING_VOLTAGE_50_LID = tempToVoltageRatio(50, R_HEATER, B_CONST_25_50, R_0_WELL);
    SWITCHING_VOLTAGE_85_LID = tempToVoltageRatio(85, R_HEATER, B_CONST_25_85, R_0_WELL);
    PCR_DEBUG("Lid 50=");
    PCR_DEBUG_LINE(SWITCHING_VOLTAGE_50_LID);
    PCR_DEBUG("Lid 85=");
    PCR_DEBUG_LINE(SWITCHING_VOLTAGE_85_LID);

#ifdef PRINT_DEBUG_CHART

    for (double v=0; v<1.0; v+=0.05) {
      double b_constant = B_CONST_HEATER;
      double temp = voltageToTemp(v, R_HEATER, b_constant, R_0_HEATER);
      PCR_DEBUG(v);
      PCR_DEBUG("\t");
      PCR_DEBUG_LINE(temp);
    }
#endif /* PRINT_DEBUG_CHART */
}
//------------------------------------------------------------------------------
HardwareStatus CLidThermistor::ReadTemp() {
    double voltageRatio;
    float lidADCValue;
    HardwareStatus result = getLidADCValue(&lidADCValue);
    if (result!=HARD_NO_ERROR) { return result; }
    voltageRatio = 1.0-lidADCValue;
    PCR_ADC_DEBUG("LidR=");
    PCR_ADC_DEBUG_LINE(voltageRatio);
    
    if (voltageRatio < 0.1) {
        // ThermistorR=0 (Short)
        return HARD_ERROR_LID_THERMISTOR_SHORT;
    }
    if (voltageRatio > 0.97) {
        // ThermistorR=INF (Thermistor is disconnected)
        return HARD_ERROR_LID_THERMISTOR_DISCONNECTED;
    }
    float b_constant;
    
    if (voltageRatio > SWITCHING_VOLTAGE_50_LID)
        b_constant = B_CONST_25_50;
    else if (voltageRatio > SWITCHING_VOLTAGE_85_LID)
        b_constant = B_CONST_25_85;
    else
        b_constant = B_CONST_25_100;

    b_constant = B_CONST_HEATER;
    float temp = voltageToTemp (voltageRatio, R_HEATER, b_constant, R_0_HEATER);
    //double thermistorR = resistance * voltageRatio / (1.0 - voltageRatio);
    iTemp = temp;
    return HARD_NO_ERROR;
}

////////////////////////////////////////////////////////////////////
// Class CPlateThermistor
static double SWITCHING_VOLTAGE_50_LOWMODE = 0;
static double SWITCHING_VOLTAGE_85_LOWMODE = 0;
static double SWITCHING_VOLTAGE_50_HIGHMODE = 0;
static double SWITCHING_VOLTAGE_85_HIGHMODE = 0;

void printVoltageTempTable () {
    PCR_DEBUG("SWITCHING_VOLTAGE_50_LOWMODE=");
    PCR_DEBUG_LINE(SWITCHING_VOLTAGE_50_LOWMODE*3.3);
    PCR_DEBUG("SWITCHING_VOLTAGE_85_LOWMODE="); 
    PCR_DEBUG_LINE(SWITCHING_VOLTAGE_85_LOWMODE*3.3);

    PCR_DEBUG("SWITCHING_VOLTAGE_50_HIGHMODE="); PCR_DEBUG_LINE(SWITCHING_VOLTAGE_50_HIGHMODE*3.3);
    PCR_DEBUG("SWITCHING_VOLTAGE_85_HIGHMODE="); PCR_DEBUG_LINE(SWITCHING_VOLTAGE_85_HIGHMODE*3.3);
    double resistance = 0;
    PCR_DEBUG_LINE("HIGH");
    for (double v=0; v<3.3; v+=0.1) {
      double b_constant;
      double voltageRatio = v/3.3;
      resistance = R_HIGH_TEMP;
      if (voltageRatio > SWITCHING_VOLTAGE_50_HIGHMODE)
          b_constant = B_CONST_25_50;
      else if (voltageRatio > SWITCHING_VOLTAGE_85_HIGHMODE)
          b_constant = B_CONST_25_85;
      else
          b_constant = B_CONST_25_100;
      double temp = voltageToTemp (voltageRatio, resistance, b_constant, R_0_WELL);
      PCR_DEBUG(v);PCR_DEBUG("\t");PCR_DEBUG_LINE(temp);
    }
    PCR_DEBUG_LINE("LOW");
    for (double v=0; v<3.3; v+=0.1) {
      double b_constant;
      double voltageRatio = v/3.3;
      resistance = R_LOW_TEMP;
      if (voltageRatio > SWITCHING_VOLTAGE_50_LOWMODE)
          b_constant = B_CONST_25_50;
      else if (voltageRatio > SWITCHING_VOLTAGE_85_LOWMODE)
          b_constant = B_CONST_25_85;
      else
          b_constant = B_CONST_25_100;
      double temp = voltageToTemp (voltageRatio, resistance, b_constant, R_0_WELL);
      PCR_DEBUG(v);PCR_DEBUG("\t");PCR_DEBUG_LINE(temp);
    }

}

CPlateThermistor::CPlateThermistor() :
        iTemp(0.0) {
    // ADC setup
    initADC();

    SWITCHING_VOLTAGE_50_LOWMODE = tempToVoltageRatio(50, R_LOW_TEMP, B_CONST_25_50, R_0_WELL);
    SWITCHING_VOLTAGE_85_LOWMODE = tempToVoltageRatio(85, R_LOW_TEMP, B_CONST_25_85, R_0_WELL);
    SWITCHING_VOLTAGE_50_HIGHMODE = tempToVoltageRatio(50, R_HIGH_TEMP, B_CONST_25_50, R_0_WELL);
    SWITCHING_VOLTAGE_85_HIGHMODE = tempToVoltageRatio(85, R_HIGH_TEMP, B_CONST_25_85, R_0_WELL);

    pinMode(PIN_WELL_HIGH_TEMP, OUTPUT);
    pinMode(PIN_WELL_HIGH_TEMP, LOW);
}
//------------------------------------------------------------------------------

void CPlateThermistor::start() {
    // ADC setup
    initADC();
    
#ifdef PRINT_DEBUG_CHART
    printVoltageTempTable();
#endif
}
bool isHighTempMode = false;
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

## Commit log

2013-06-19 Add Arduino Source Files
2013-06-19 Adjust margin of device list
2013-06-27 upload 2d/3d parts
    [Coolers.dwg, Power.dwg, n101_cover_back.dwg, n102_cover_front.dwg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]
2013-06-27 add 3d models
    [202_Heater.dwg, 204_felt.dwg, 205_spacer_201_203.dwg, 207_M3_screw_203.dwg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]
2013-07-05 add stl&igs data
    [202_Heater.igs, 202_Heater.stl, 204_felt.igs, 204_felt.stl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]
2013-07-17 debug resistance
2013-07-17 update resistance param to unsigned long
2013-07-21 remove resistance sysout
2013-07-23 UNOテスト用 / Leonardo対応による不具合を修正
2013-07-31 add latest eagle files
    [OpenPCR-combined-blockfront.brd, OpenPCR-combined-blockfront.sch]
2013-07-31 温度パラメタを更新
2013-08-02 Sefial Timeout (avoid continuous cooling & heating after disconnection)
2013-08-05 Set visibility of the "Unplugged" dialog right after a device is found.
2013-08-07 Remove useless println
2013-10-07 add vertical coolers because it's cheaper!
    [Coolers_Vertical.f3d]
2013-10-07 export sat/step/stl formats to test whether it's possible to design both in Mac and Win
    [Coolers_Vertical.step, Coolers_Vertical.stl]
2013-10-07 add Vertical Cooler to save money
    [Coolers_Vertical.dwg, Coolers_Vertical.f3d, Coolers_Vertical.step, Coolers_Vertical.stl]
2013-10-09 adding DeepCooler
    [Coolers_Vertical.dwg]
2013-11-06 ready to cut
2013-11-14 update to cut
2014-07-26 moving to fusion360
    [BrainBoard.dwg, Heatsink.dwg, Hinge-UK.dwg, Hinge-hands.dwg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]
2014-07-26 moving to fusion 360
    [AL-heater8.dwg, AL-pad-between-heatsink-and-well.dwg, AL-well.dwg, Felt-for-well.dwg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]
2014-07-26 move to fusion 360
    [ST-cover-ver1.dwg]
2015-08-04 add pcbs
    [NinjaPCR-131101.brd, NinjaPCR-131101.sch, NinjaPCR-131202.brd, NinjaPCR-131202.sch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]
2015-08-04 refresh all data to latest
    [202_Heater.dwg, 202_Heater.igs, 202_Heater.stl, 204_felt.dwg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]
2015-10-19 remove unused pcbs
    [NinjaPCR-131202-USEME.brd, NinjaPCR-131202-USEME.sch, NinjaPCR-140720.brd, NinjaPCR-140720.sch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]
2015-10-20 rename for easy understanding
    [NinjaPCB-131202.brd, NinjaPCB-131202.sch, NinjaPCB-PowerSupplyVersion.brd, NinjaPCB-PowerSupplyVersion.sch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]
2015-12-18 export lasercut data as ai and pdf
2016-01-06 add values of reg&cap
    [NinjaPCB-131202.brd, NinjaPCB-131202.sch]
2016-11-12 Use same values in sch and brd
    [NinjaPCB-131202.brd, NinjaPCB-131202.sch]
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2016-11-20 CAM of well added
    [AL002-well-with-CAM.f3d]
2016-11-26 update toolpath Tube2
    [AL002-well-with-CAM.f3d]
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2017-09-02 preparing NinjaPCB ver2 using Seeed OPL
    [NinjaPCB_ver2-170831.brd, NinjaPCB_ver2-170831.sch]
2017-09-02 fixing things
    [NinjaPCB_ver2-170831.brd, NinjaPCB_ver2-170831.sch]
2017-09-28 add evaluation board for NinjaPCB ver2
    [NinjaPCB_ver2-170831.brd, NinjaPCB_ver2-170831.sch]
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2017-10-06 completed ver2-170831
    [NinjaPCB_ver2-170831.brd, NinjaPCB_ver2-170831.sch]
2017-10-09 ordered pcb
    [NinjaPCB_ver2-170831.brd]
2017-12-01 remove ver2 temporary. it will be back after evaluation.
    [NinjaPCB_ver2-170831.brd, NinjaPCB_ver2-170831.sch]
2018-01-11 pushed again to share with mariko. do not manufacture it yet
    [NinjaPCB_ver2-170831.brd, NinjaPCB_ver2-170831.sch]
2018-01-16 add memos
    [NinjaPCB_ver2-180115.sch]
2018-01-17 pulldown HEATER to write
    [NinjaPCB_ver2-170831.sch, NinjaPCB_ver2-180115.sch]
2018-01-17 VNH5019 doesnot have same pinout as VNH3SP30
    [NinjaPCB_ver2-170831.brd, NinjaPCB_ver2-170831.sch, NinjaPCB_ver2-180115.sch]
2018-01-29 use relay instead of driver
    [NinjaPCB_ver2-180115.sch]
2018-01-29 add ESP-12F-breakout compatible with ESP-WROOM-02-breakout
    [ESP-12F-BREAK.brd, ESP-12F-BREAK.sch, ESP-WROOM-02-BREAK.sch, NinjaPCB_ver2-180115.sch]
2018-01-29 use breakout board
    [NinjaPCB_ver2-180115.sch]
2018-02-08 latest updates
    [ESP-12F-ASIF-WR02.brd, ESP-12F-ASIF-WR02.sch, ESP-WROOM-02-ASIF-12.brd, ESP-WROOM-02-ASIF-12.sch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]
2018-02-27 Designing 2nd ver2 board. DO NOT make first NinjaPCB_ver2-170831.brd
    [NinjaPCB_ver2-180115.brd]
2018-03-03 remove errored one
    [NinjaPCB_ver2-170831.brd, NinjaPCB_ver2-170831.sch]
2018-03-03 to be ordered
    [NinjaPCB_ver2-180115.brd, NinjaPCB_ver2-180115.sch]
2018-03-04 npn to pnp. added pullups and pulldowns
    [NinjaPCB_ver2-180115.brd, NinjaPCB_ver2-180115.sch]
2018-03-04 added hole for gromet #digikey 36-733-ND
    [NinjaPCB_ver2-180115.brd]
2018-03-08 version control
    [NinjaPCB-ver1.0-PowerSupply.brd, NinjaPCB-ver1.0-PowerSupply.sch, NinjaPCB-ver1.0.brd, NinjaPCB-ver1.0.sch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]
2018-03-08 changed R14 into RT. no reason for T
    [NinjaPCB_ver2.2.sch]
2018-03-08 add low ESR cap to standard voltage for NAU7802
    [NinjaPCB_ver2.2.sch]
2018-03-09 Support Relay (for replacement of motor driver IC)
2018-03-13 replace 2d data to ver2 dxf
    [NinjaPCB_ver2.2.sch, w1001_heater-lift.dxf, w1002_cover-top.dxf, w1003_cover-back.dxf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]
2018-03-15 add MODE jumper to use same source for 4x4 and 2x2
    [NinjaPCB_ver2.2.sch]
2018-03-15 add MooMoo ones
    [NinjaPCB_ver2.2.sch, w1001_heater-lift.dxf, w1002_cover-top.dxf, w1003_cover-back.dxf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]
2018-03-16 split into 2 subprojects : 4x4 NinNin and 2x2 MooMoo
    [NinjaPCB_ver2.2.sch, w1001_heater-lift.dxf, w1002_cover-top.dxf, w1003_cover-back.dxf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]
2018-03-17 use easier parts. add notes to design
    [NinjaPCB_ver2.1.brd, NinjaPCB_ver2.1.sch, NinjaPCB_ver2.2.sch]
2018-03-18 abstract layout image of 2x2MooMoo
    [NinjaPCB-2x2-MooMoo-logic_ver2.0.brd, NinjaPCB-2x2-MooMoo-logic_ver2.0.sch, NinjaPCB-2x2-MooMoo-power_ver2.0.brd, NinjaPCB-2x2-MooMoo-power_ver2.0.sch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]
2018-03-22 change values of MOSFET G-S reg
    [NinjaPCB-2x2-MooMoo-power_ver2.0.brd, NinjaPCB-2x2-MooMoo-power_ver2.0.sch, NinjaPCB-4x4-NinNin_ver2.0.sch, NinjaPCB_ver2.1.brd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]
2018-03-26 start wiring NinNin ver2.0
    [NinjaPCB-2x2-MooMoo-logic_ver2.0.brd, NinjaPCB-2x2-MooMoo-logic_ver2.0.sch, NinjaPCB-2x2-MooMoo-power_ver2.0.brd, NinjaPCB-2x2-MooMoo-power_ver2.0.sch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]
2018-03-30 dru clear
    [NinjaPCB-4x4-NinNin_ver2.0.brd]
2018-03-30 minor tunes
    [NinjaPCB-4x4-NinNin_ver2.0.brd]
2018-03-31 ready to order
    [NinjaPCB-4x4-NinNin_ver2.0.GBL, NinjaPCB-4x4-NinNin_ver2.0.GBO, NinjaPCB-4x4-NinNin_ver2.0.GBS, NinjaPCB-4x4-NinNin_ver2.0.GTL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]
2018-04-01 panelized NinNin
    [NinjaPCB-2x2-MooMoo_ver2.0.sch, NinjaPCB-4x4-NinNin_ver2.0-panel2x3-GTP.brd, NinjaPCB-4x4-NinNin_ver2.0-panel2x3.brd, NinjaPCB-4x4-NinNin_ver2.0.GBL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]
2018-04-01 prepare for order
    [NinjaPCB-2x2-MooMoo_ver2.0.sch]
2018-04-08 shrink panel
    [Thermistor-Connector-panel10x6.brd, Thermistor-Connector-panel5x3.brd]
2018-04-11 set distance more equal 10mil for 2oz at Seeed
    [NinjaPCB-4x4-NinNin_ver2.0-panel2x3.brd, NinjaPCB-4x4-NinNin_ver2.0.brd]
2018-04-18 set default 4x4
    [NinjaPCB-2x2-MooMoo_ver2.0.sch, NinjaPCB-4x4-NinNin_ver2.0.brd, NinjaPCB-4x4-NinNin_ver2.0.sch, NinjaPCB_ver1.0-PowerSupply.brd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]
2018-04-19 remove wrong schematics
    [EN2-EP2.brd, EN2-EP2.sch, NinjaPCB_ver2.0.brd, NinjaPCB_ver2.0.sch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]
2018-04-26 Update lasercut data
    [2x-w1005_cover-sides.dxf, 2x-w2008_body-hinges.dxf, 2x-w2009_body-hinge-shafts.dxf, 3x-w1007_lid-hinges.dxf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]
2018-04-26 update 2d/3d info
    [AL002-well-with-CAM.f3d]
2018-05-01 CDN test
    [NinjaPCB_ver2.1.sch]
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2018-05-14 Fixed board config according to 2.0 schematics
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2018-05-14 update dxf
    [2x-w1005_cover-sides.dxf, 2x-w2009_body-hinge-shafts.dxf, 3x-w1007_lid-hinges.dxf, NinjaPCB_ver2.1.sch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]
2018-05-21 ver2.1 finished
    [DIN4-break.brd, DIN4-break.sch, NinjaPCB_ver2.1.GBL, NinjaPCB_ver2.1.GBO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]
2018-05-23 minor update of silk
    [NinjaPCB_ver2.1.brd, NinjaPCB_ver2.1.sch, NinjaPCR-seeedbom.xlsx]
2018-05-25 minor update for layout
    [NinjaPCB_ver2.1.brd, NinjaPCB_ver2.1.sch]
2018-06-03 ignore autogen backup files of CorelDRAW
    [w1001.dxf, w1002.dxf, w1003-kit.dxf, w1004-kit.dxf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]
2018-06-18 update laser
    [w2001-LGA115x.dxf, w2001-LGA775.dxf, w2003.dxf, w2004.dxf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]
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2018-06-30 NinjaPCB ver2.2
    [NinjaPCB_ver2.2.brd, NinjaPCB_ver2.2.sch]
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2018-07-19 update front panel
    [w2003-maker.dxf]
2018-07-23 add NinjaPCR 2.2
    [NinjaPCB_ver2.2.brd, NinjaPCB_ver2.2.sch]
2018-07-23 fixed NinjaPCB ver 2.2
    [NinjaPCB_ver2.2.GTP, NinjaPCB_ver2.2.brd, NinjaPCB_ver2.2.sch, writer2.brd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]
2018-07-24 updated 2.2
    [NinjaPCB_ver2.2.brd, NinjaPCB_ver2.2.sch, writer2.brd, writer2.sch]
2018-07-24 fixed 2.2
    [NinjaPCB_ver2.2.sch]
2018-08-20 add models
    [a1001.f3d, a1001.iges, a1001.step]
2018-08-27 update words
    [ESP-WRITE.brd, ESP-WRITE.sch]
2018-08-27 remove ver1.0
    [NinjaPCB-131202.brd, NinjaPCB-131202.sch, NinjaPCB-PowerSupplyVersion.brd, NinjaPCB-PowerSupplyVersion.sch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]
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2020-10-29 Add version / Fix "Error9" on very low temperature
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2021-04-16 found another relay to H bridge but not wired
    [NinjaPCB_ver2.2-B_Mask.gbs, NinjaPCB_ver2.2-B_Paste.gbp, NinjaPCB_ver2.2-B_SilkS.gbo, NinjaPCB_ver2.2-Bottom.gbl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]
2021-04-16 add link
    [NinjaPCB_ver2.3.sch]
2021-05-10 add front panel to print for maker model
    [w2003a_body-front-ver2.1-maker.stl]

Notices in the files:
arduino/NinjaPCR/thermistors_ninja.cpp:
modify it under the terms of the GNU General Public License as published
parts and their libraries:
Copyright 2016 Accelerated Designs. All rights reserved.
